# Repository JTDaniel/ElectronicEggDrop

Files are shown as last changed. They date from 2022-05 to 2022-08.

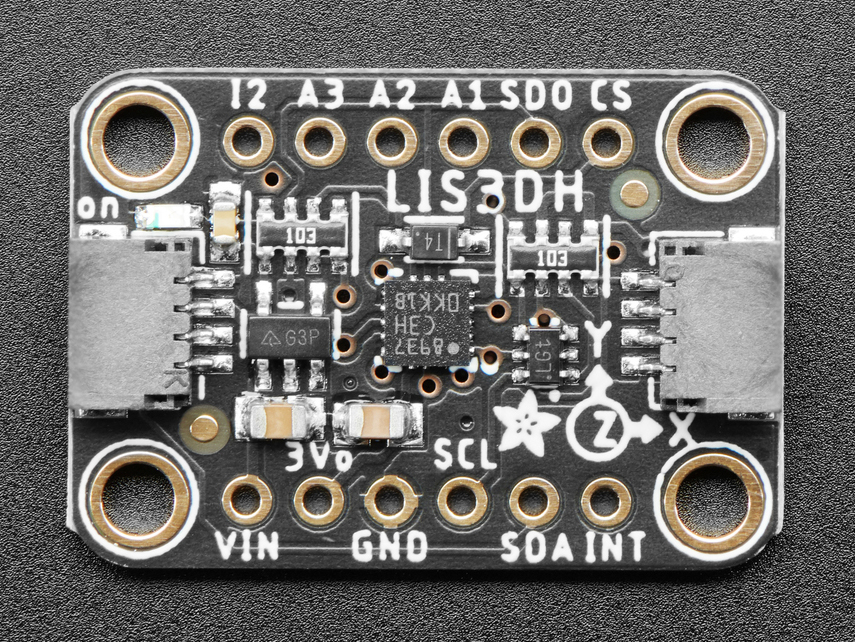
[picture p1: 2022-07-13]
Electronics/ImportedParts/Adafruit-LIS3DH-Breakout-PCB/Adafruit-LIS3DH-Breakout-PCB-master/assets/2809.jpg

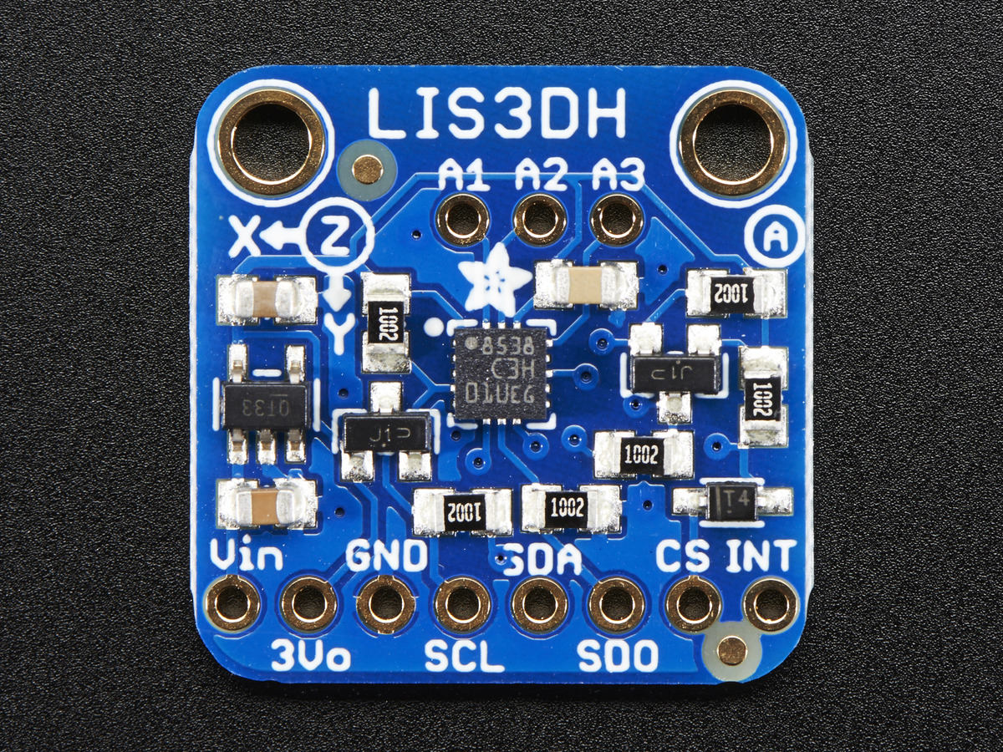
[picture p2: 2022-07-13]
Electronics/ImportedParts/Adafruit-LIS3DH-Breakout-PCB/Adafruit-LIS3DH-Breakout-PCB-master/assets/image.jpg

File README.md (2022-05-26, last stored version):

# ElectronicEggDrop
This is a project Pioneered by the Arizona State University MakerSpace workers, J. Travis Daniel, Gehrig Dixon, and Liam Nelson.  The goal is to make an egg drop experiment that is more sustainable than the regular use of this experiment in physics classrooms today.  This is being done by replacing regular edible egss with electronic sensor packages designed to look like an egg.

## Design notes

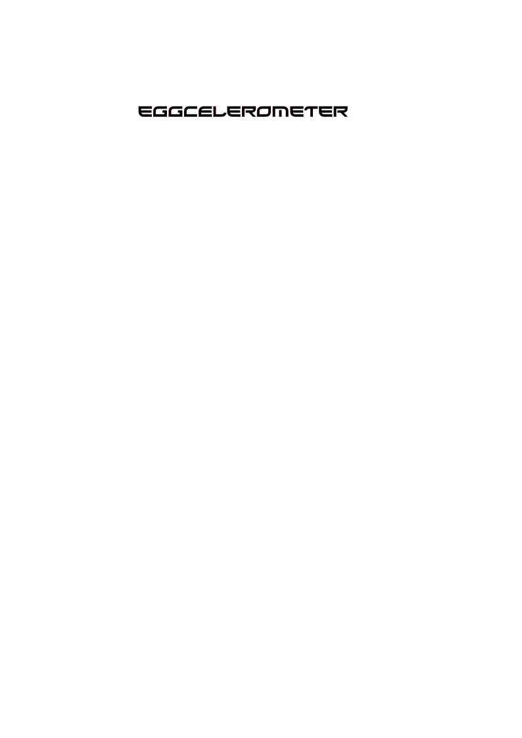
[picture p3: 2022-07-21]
Electronics/Graphics/Eggcelerometer.png

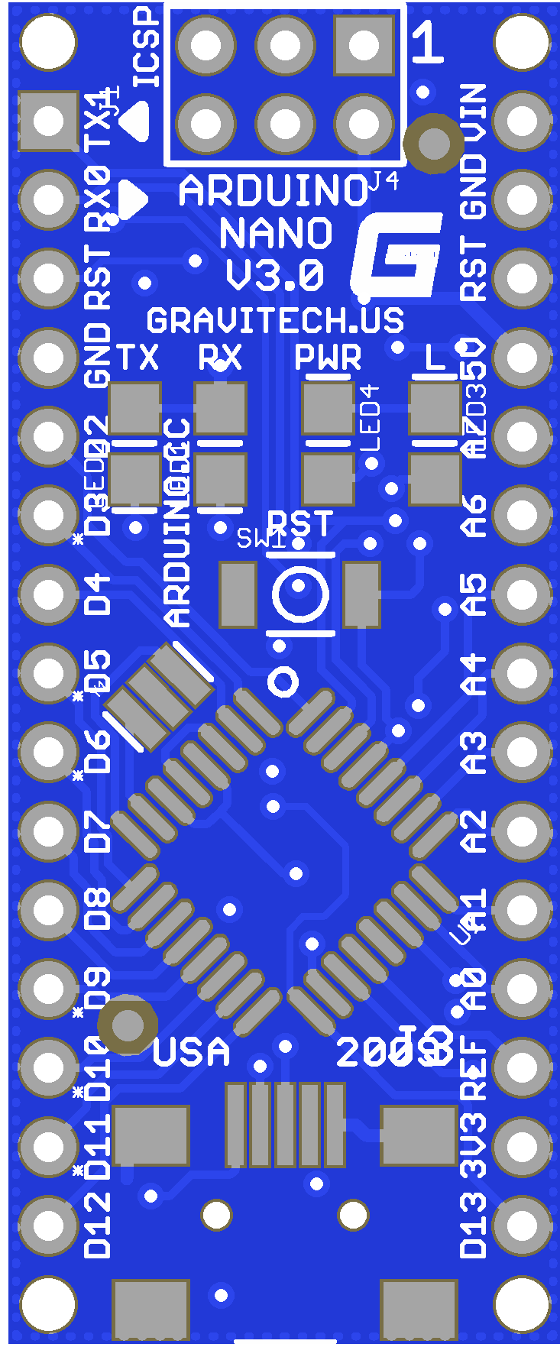
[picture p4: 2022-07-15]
3D_Models/Arduino Nano/Arduino Nano.png

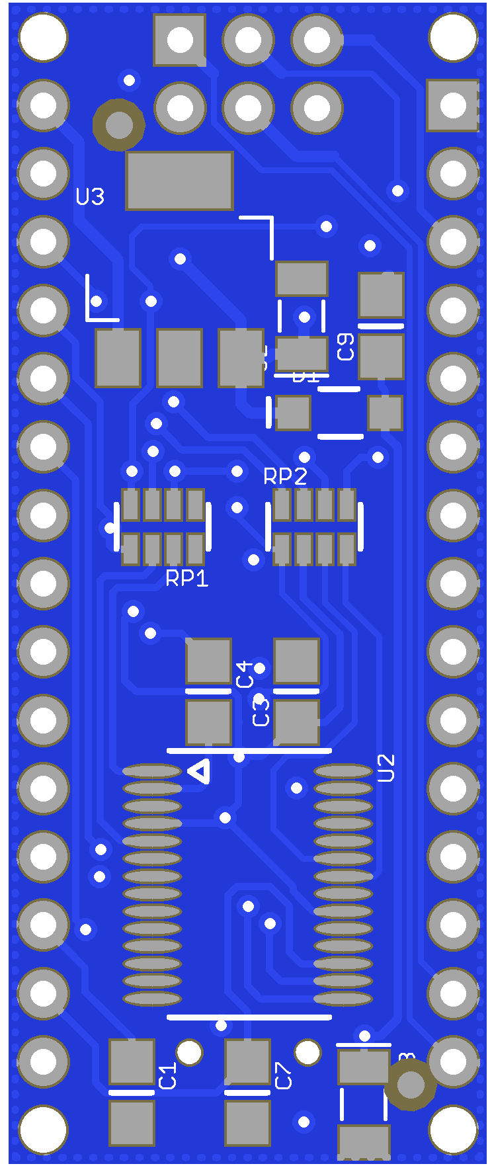
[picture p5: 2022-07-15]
3D_Models/Arduino Nano/Arduino Nano .png

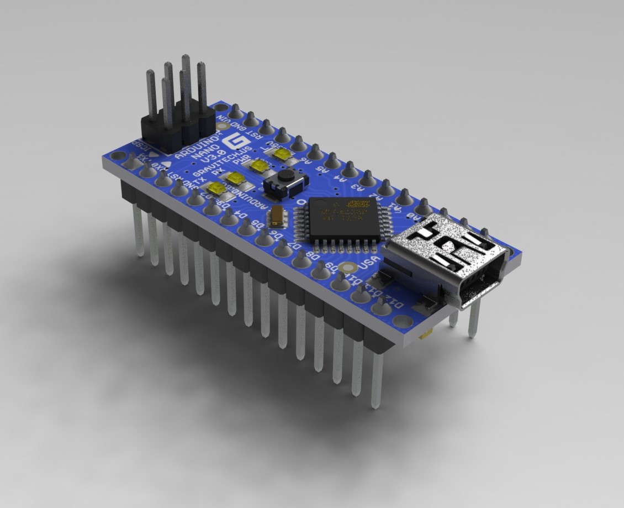
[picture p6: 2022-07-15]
3D_Models/Arduino Nano/Arduino Nano.JPG

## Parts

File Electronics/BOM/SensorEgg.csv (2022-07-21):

Id | Designator | Package | Quantity | Designation | Supplier and ref
1 | LIS3DH Connector,SD Card Reader Connector | PinHeader_1x06_P2.54mm_Vertical | 2 | Conn_01x06
2 |  |  | 1
3 | U1 | LIS3DH | 1 | LIS3DH
4 | U2 | SDCardReader | 1 | SDCardReader

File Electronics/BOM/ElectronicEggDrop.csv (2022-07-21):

Id | Designator | Package | Quantity | Designation | Supplier and ref
1 | Arduino Nano | MODULE_ABX00053 | 1 | ABX00053
2 | +3.7v,+3.7V | JST_PH_S2B-PH-K_1x02_P2.00mm_Horizontal | 2 | Screw_Terminal_01x02
3 | R2,R3,R1 | R_Axial_DIN0204_L3.6mm_D1.6mm_P5.08mm_Horizontal | 3 | R
4 | Indicator_LEDs1 | PinSocket_2x03_P2.54mm_Vertical | 1 | LED_RAGB
5 | Switch | PinSocket_1x02_P2.54mm_Vertical | 1 | SW_SPST
6 | LIS3DH Connector,SD Card Reader Connector | PinSocket_1x06_P2.54mm_Vertical | 2 | Conn_01x06_Male

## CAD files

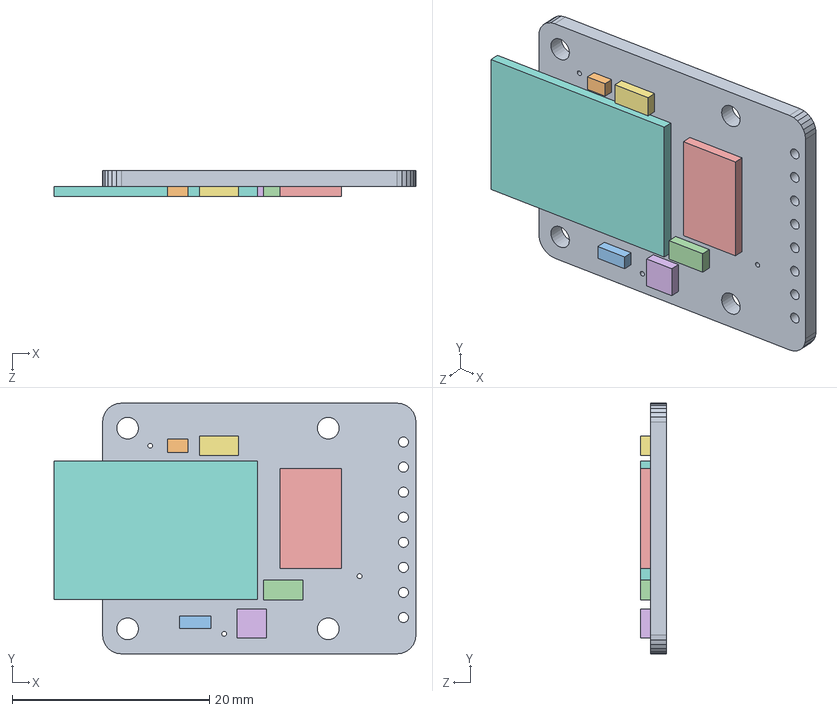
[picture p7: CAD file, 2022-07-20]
3D_Models/microsd/microsd.SLDASM
36.7 x 25.4 x 2.60 mm
microsd
CHIPLED0805_RED
A_321618R_10UF_10V
C0805K_0_1UF
SO16_4050D
SOT235L_LP298XS
R0805_1K
MICROSD_MICROSD

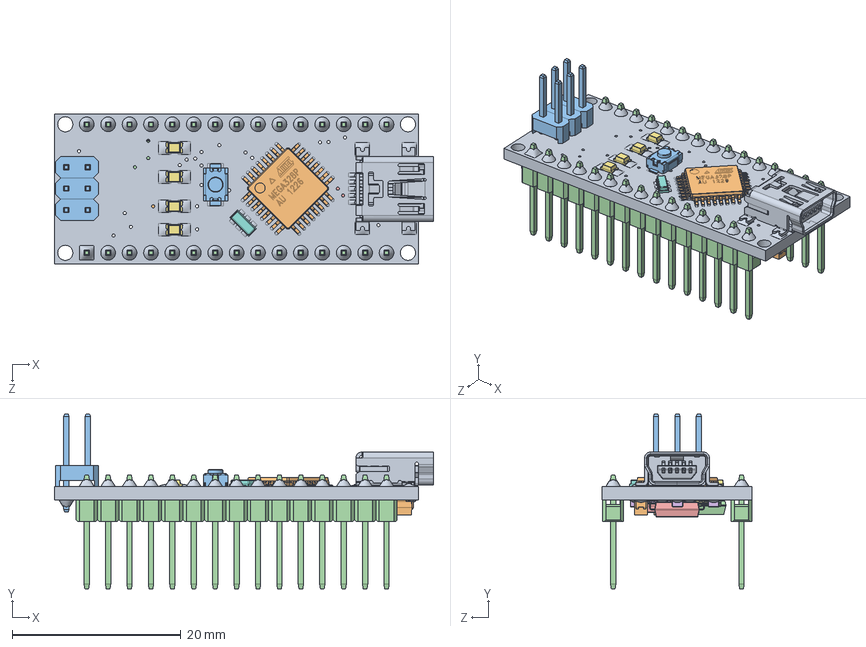
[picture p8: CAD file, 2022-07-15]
3D_Models/Arduino Nano/Arduino nano.SLDASM
45.0 x 20.7 x 17.8 mm
nano board
atmega328
PLD-2.step x 3
1x15 Male Pin Header x 2
FTDI FT232RL
User Library-C0805-2.step x 5
0805 Chip SMD LED (2x1.2mm).step x 4
SMD Crystal 16MHz
Mini B USB
Tantalum Capacitor 475C A3216 x 2
Pushbutton3x4x2
C5 FD10 Reg
Diode MBR0520
102 RESISTOR PACK
189 RESISTOR PACK

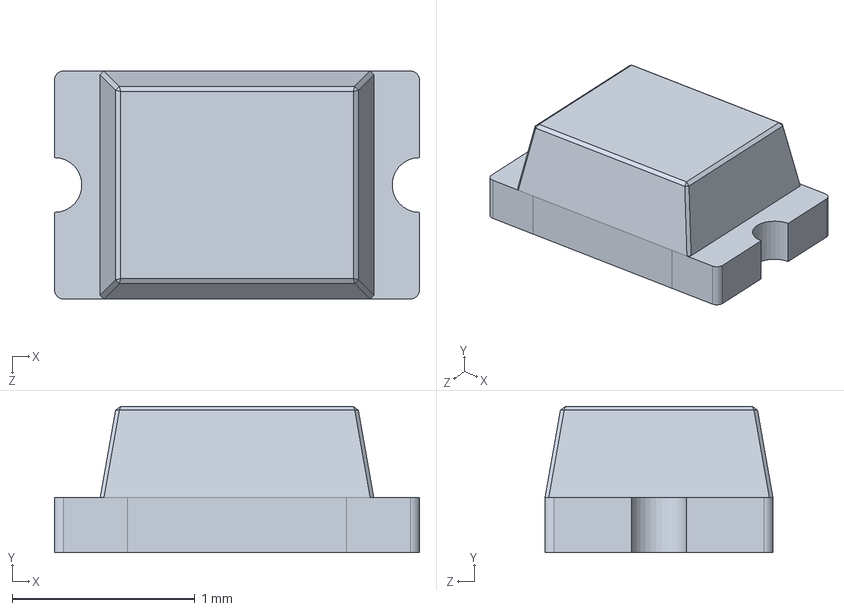
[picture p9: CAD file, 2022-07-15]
3D_Models/Arduino Nano/0805 Chip SMD LED (2x1.2mm).step.SLDPRT
2.00 x 0.8 x 1.25 mm

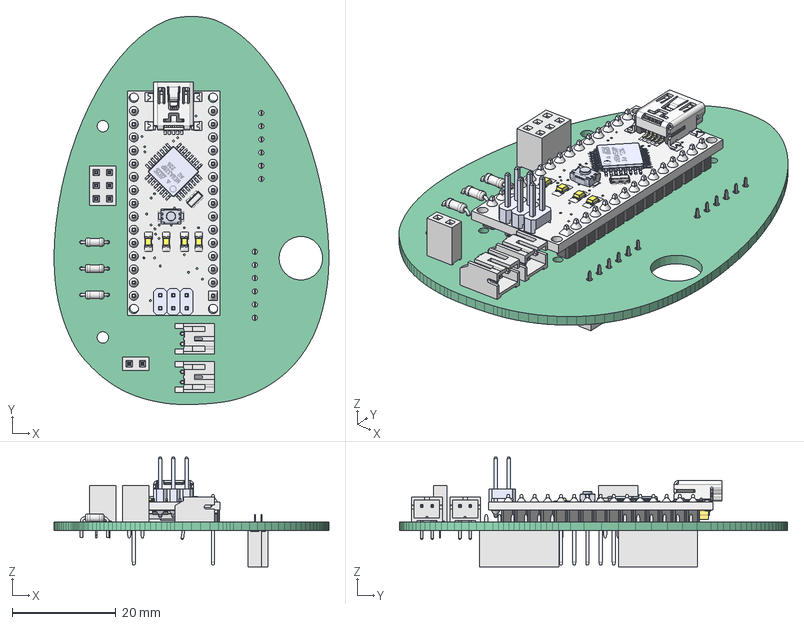
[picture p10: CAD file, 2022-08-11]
3D_Models/ControlEgg.FCStd
52.9 x 74.6 x 21.1 mm
Pcb_7da9
nano board
atmega328
PLD-2.step
PLD-2.step001
PLD-2.step002
1x15 Male Pin Header
1x15 Male Pin Header001
1x15 Male Pin Header002
1x15 Male Pin Header003
1x15 Male Pin Header004
1x15 Male Pin Header005
1x15 Male Pin Header006
1x15 Male Pin Header007
1x15 Male Pin Header008
1x15 Male Pin Header009
1x15 Male Pin Header010
1x15 Male Pin Header011
1x15 Male Pin Header012
1x15 Male Pin Header013
1x15 Male Pin Header014
1x15 Male Pin Header015
1x15 Male Pin Header017
1x15 Male Pin Header018
1x15 Male Pin Header019
1x15 Male Pin Header020
1x15 Male Pin Header021
1x15 Male Pin Header022
1x15 Male Pin Header023
1x15 Male Pin Header024
1x15 Male Pin Header025
1x15 Male Pin Header026
1x15 Male Pin Header027
1x15 Male Pin Header028
1x15 Male Pin Header029
1x15 Male Pin Header030
1x15 Male Pin Header031
1x15 Male Pin Header032
FTDI FT232RL
FTDI FT232RL001
FTDI FT232RL002
FTDI FT232RL003
FTDI FT232RL004
FTDI FT232RL005
FTDI FT232RL006
FTDI FT232RL007
FTDI FT232RL008
FTDI FT232RL009
FTDI FT232RL010
FTDI FT232RL011
FTDI FT232RL012
FTDI FT232RL013
FTDI FT232RL014
FTDI FT232RL015
FTDI FT232RL016
FTDI FT232RL017
FTDI FT232RL018
FTDI FT232RL019
FTDI FT232RL020
FTDI FT232RL021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

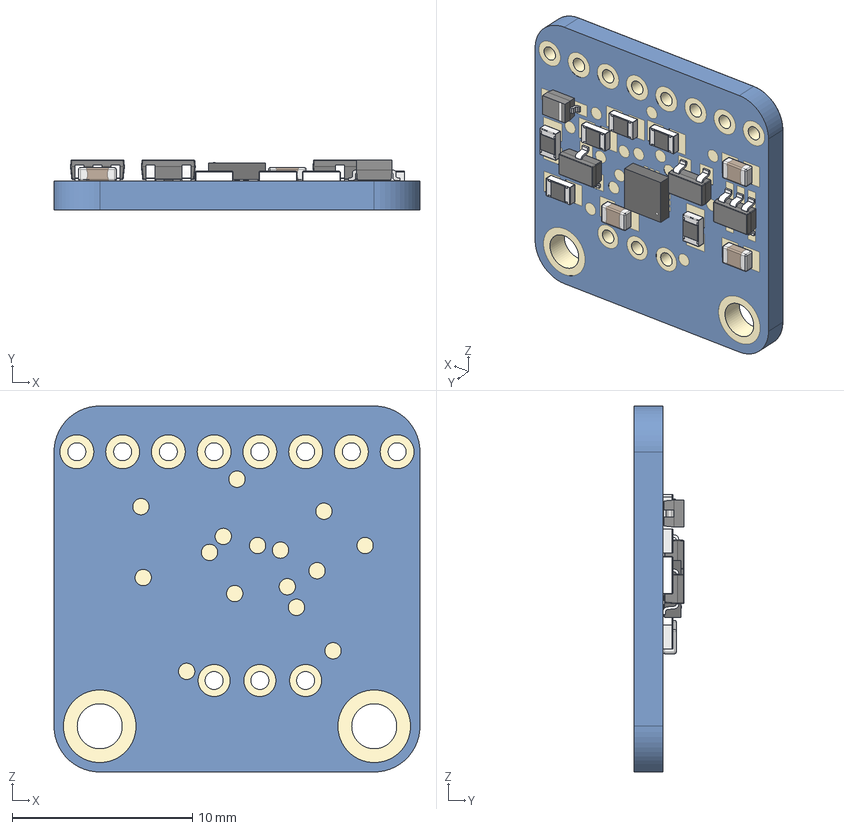
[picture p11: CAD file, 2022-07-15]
3D_Models/LIS3DH/LIS3DH v9.step
20.3 x 2.79 x 20.3 mm
SOT23-5
SOT23-3 x 2
16-LGA-3X3
SMD Resistor 0805 x 6
Cap 0805 x 3
SOD-323

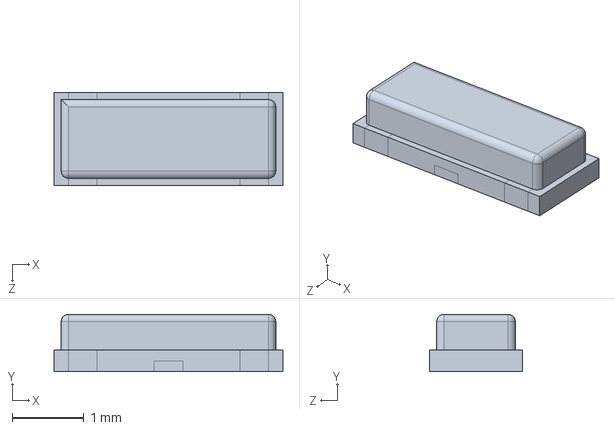
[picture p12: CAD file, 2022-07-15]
3D_Models/Arduino Nano/SMD Crystal 16MHz.SLDPRT
3.20 x 0.8 x 1.30 mm

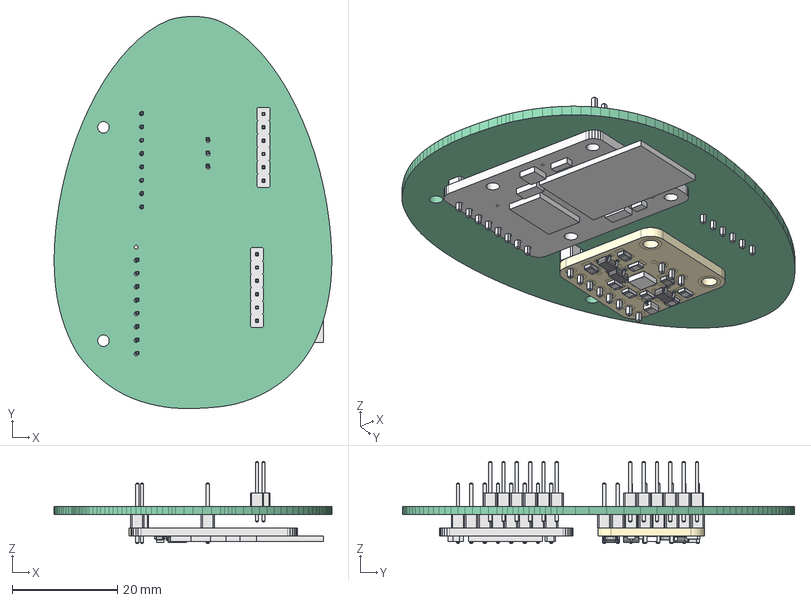
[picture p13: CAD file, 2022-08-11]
3D_Models/SensorEgg.FCStd
52.9 x 74.6 x 15.6 mm
Pcb_4512
LIS3DH Connector_PinHeader_1x06_P254mm_Vertical_2e8bbb15d2d6 x 2
SOT23-5 v1
SOT23-5 v002
SOT23-5 v003
SOT23-5 v004
SOT23-5 v005
SOT23-5 v006
SOT23-3 v1
SOT23-3 v002
SOT23-3 v003
SOT23-3 v004
SOT23-3 v006
SOT23-3 v007
SOT23-3 v008
SOT23-3 v009
16-LGA-3X3 v2
SMD Resistor 0805 v1
SMD Resistor 0805 v002
SMD Resistor 0805 v003
SMD Resistor 0805 v005
SMD Resistor 0805 v006
SMD Resistor 0805 v007
SMD Resistor 0805 v009
SMD Resistor 0805 v010
SMD Resistor 0805 v011
SMD Resistor 0805 v013
SMD Resistor 0805 v014
SMD Resistor 0805 v015
SMD Resistor 0805 v017
SMD Resistor 0805 v018
SMD Resistor 0805 v019
SMD Resistor 0805 v021
SMD Resistor 0805 v022
SMD Resistor 0805 v023
Cap 0805 v1
Cap 0805 v002
Cap 0805 v003
SOD-323 v1
U1_PinHeader_1x08_P254mm_Vertical_1ec43fbb1add[2] x 2
U1_PinHeader_1x03_P254mm_Vertical_1ec43fbb1add[3]
Ada microsd
Ada microsd001
Ada microsd002
Ada microsd003
Ada microsd004
Ada microsd005
Ada microsd006
Ada microsd007

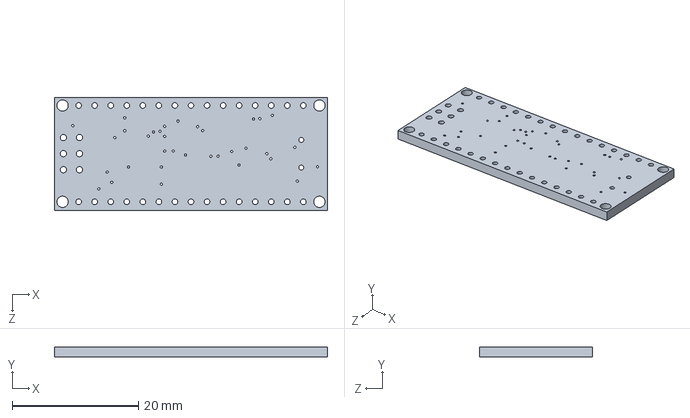
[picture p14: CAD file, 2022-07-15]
3D_Models/Arduino Nano/nano board.SLDPRT
43.2 x 1.60 x 17.8 mm

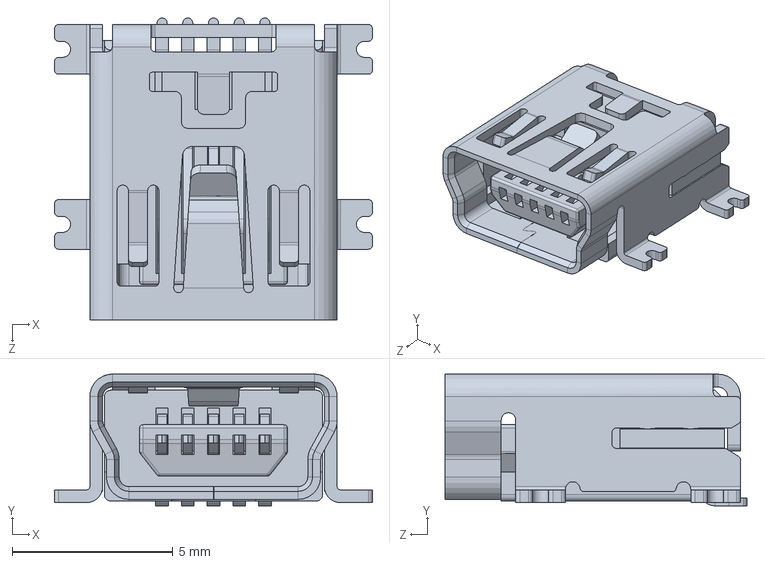
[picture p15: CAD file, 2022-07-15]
3D_Models/Arduino Nano/Mini B USB.SLDPRT
9.90 x 4.10 x 9.40 mm

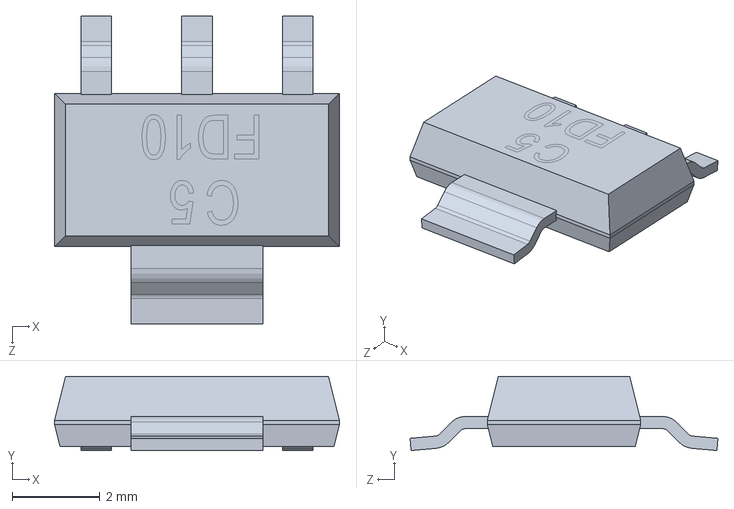
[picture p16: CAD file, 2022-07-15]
3D_Models/Arduino Nano/C5 FD10 Reg.SLDPRT
6.50 x 1.69 x 7.02 mm

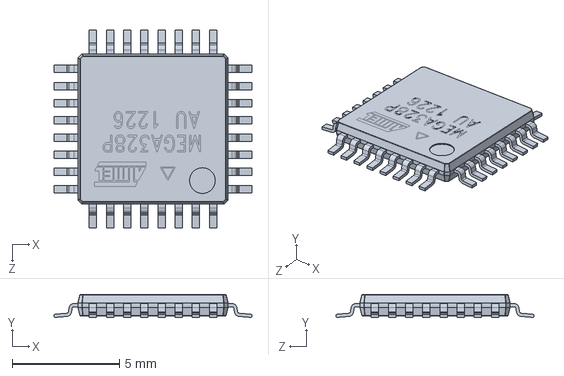
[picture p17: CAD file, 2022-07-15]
3D_Models/Arduino Nano/atmega328.SLDPRT
9.21 x 1.07 x 9.21 mm

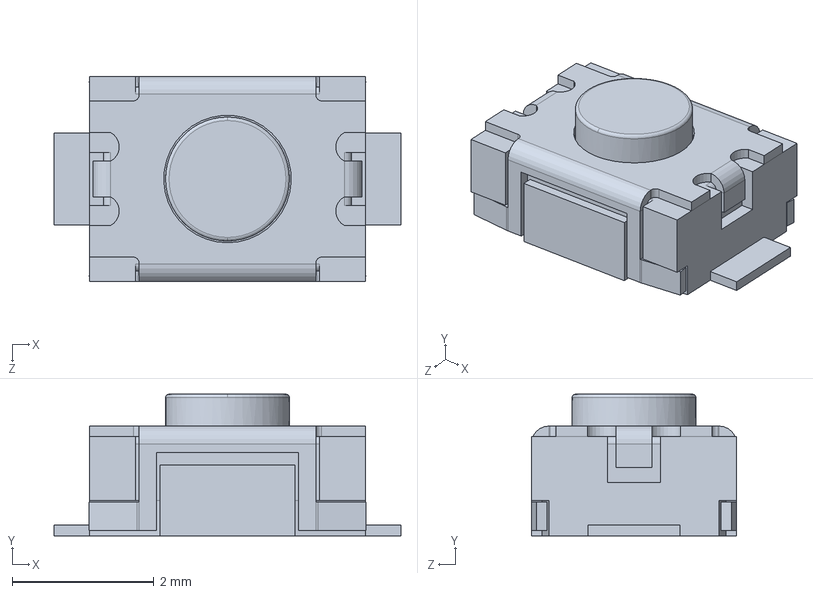
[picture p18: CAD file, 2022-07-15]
3D_Models/Arduino Nano/Pushbutton3x4x2.SLDPRT
4.90 x 2.00 x 2.90 mm

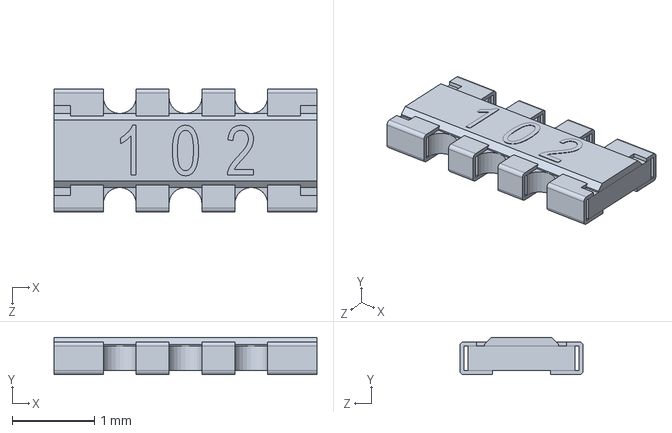
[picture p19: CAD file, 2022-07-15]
3D_Models/Arduino Nano/102 RESISTOR PACK.SLDPRT
3.20 x 0.455 x 1.50 mm

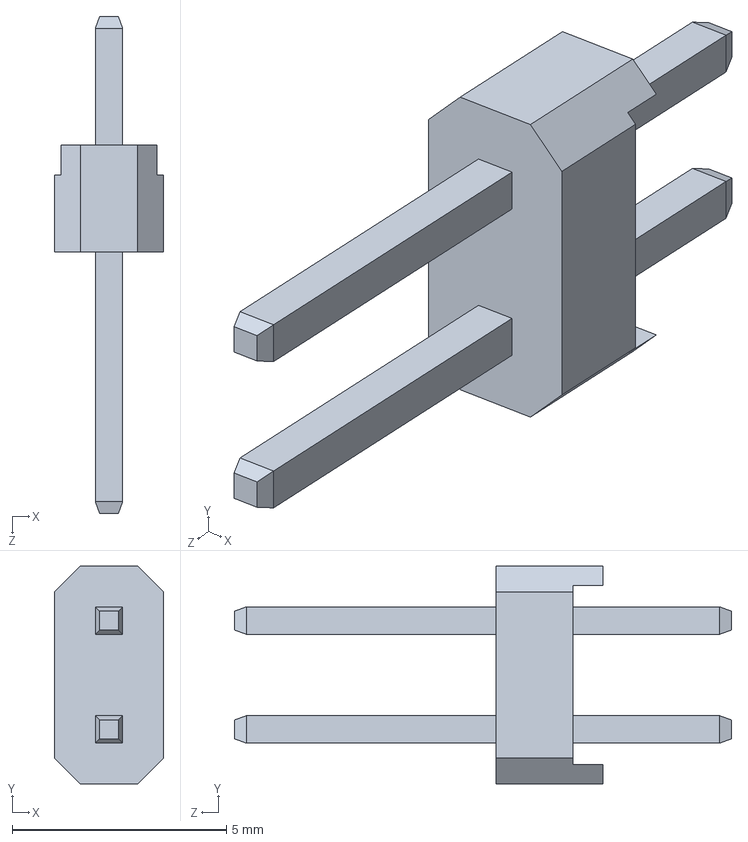
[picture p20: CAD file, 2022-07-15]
3D_Models/Arduino Nano/PLD-2.step.SLDPRT
2.54 x 5.08 x 11.6 mm

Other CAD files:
3D_Models/LIS3DH/LIS3DH.FCStd
3D_Models/microsd/Ada microsd.STEP
3D_Models/Arduino Nano/1x15 Male Pin Header.SLDPRT
3D_Models/Arduino Nano/Diode MBR0520.SLDPRT
3D_Models/Arduino Nano/189 RESISTOR PACK.SLDPRT
3D_Models/Arduino Nano/ArduinoNano.FCStd
3D_Models/Arduino Nano/FTDI FT232RL.SLDPRT
3D_Models/Arduino Nano/Tantalum Capacitor 475C A3216.SLDPRT
3D_Models/Arduino Nano/User Library-C0805-2.step.SLDPRT
3D_Models/microsd/Ada microsd.SLDPRT
Electronics/ElectronicEggDropV1/SensorEgg/SensorEgg.step

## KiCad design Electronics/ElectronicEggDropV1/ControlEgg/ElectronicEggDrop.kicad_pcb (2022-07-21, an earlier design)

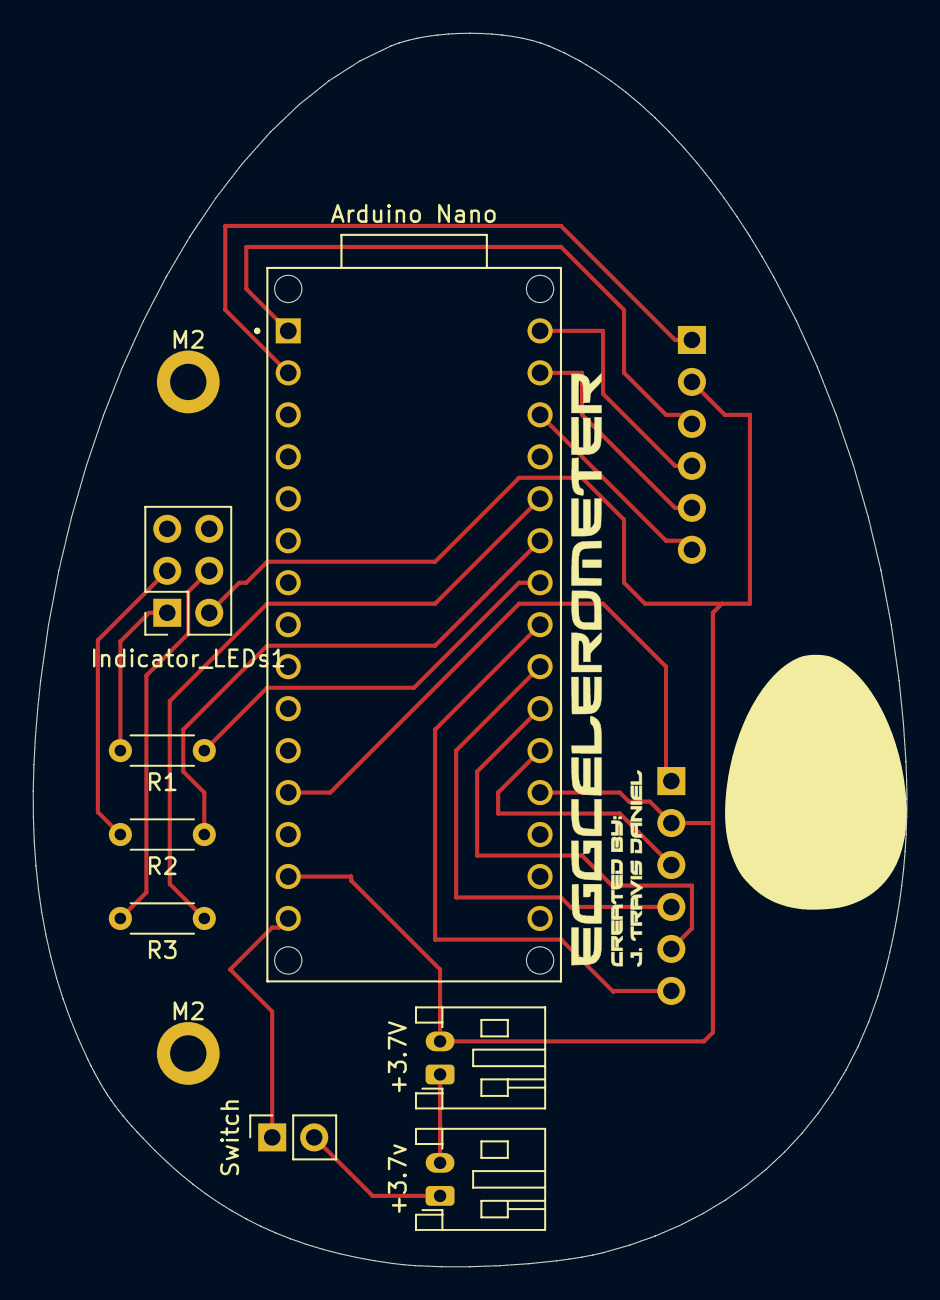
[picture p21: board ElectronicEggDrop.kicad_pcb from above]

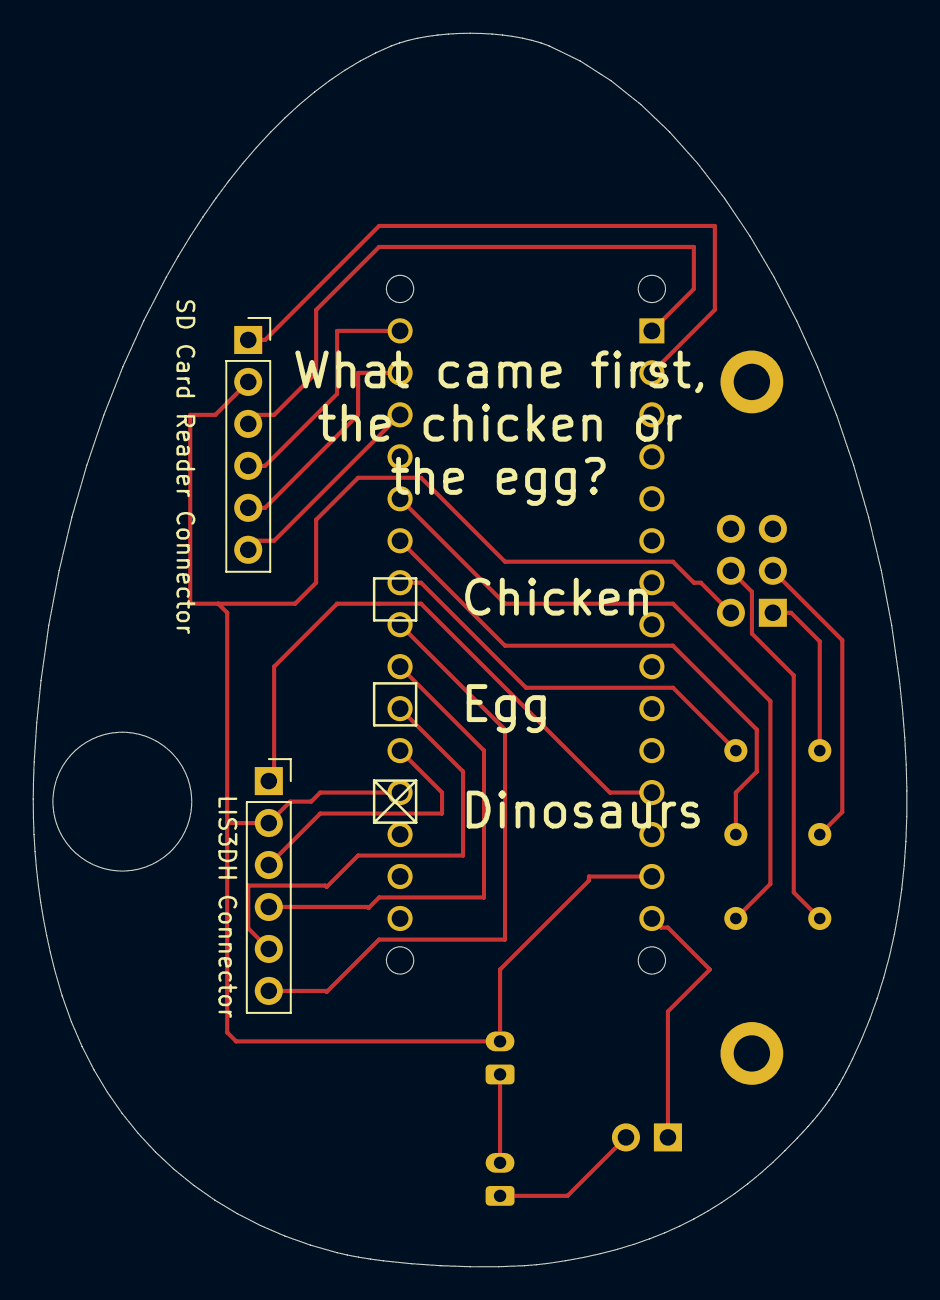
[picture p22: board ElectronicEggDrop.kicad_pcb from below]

Board: 2 copper layers, 52.9 x 74.6 mm, 10 parts (2 on the bottom side), 20 nets.

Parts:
+3.7V, +3.7v: Screw_Terminal_01x02; JST_PH_S2B-PH-K_1x02_P2.00mm_Horizontal
Arduino Nano: ABX00053; MODULE_ABX00053
Indicator_LEDs1: LED_RAGB; PinSocket_2x03_P2.54mm_Vertical
LIS3DH Connector: Conn_01x06_Male; PinSocket_1x06_P2.54mm_Vertical
R1, R2, R3: R; R_Axial_DIN0204_L3.6mm_D1.6mm_P5.08mm_Horizontal
SD Card Reader Connector: Conn_01x06_Male; PinSocket_1x06_P2.54mm_Vertical
Switch: SW_SPST; PinSocket_1x02_P2.54mm_Vertical

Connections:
GND: +3.7V.2, Arduino Nano.14 (GND), Arduino Nano.19 (GND), Indicator_LEDs1.2 (A), LIS3DH Connector.2, SD Card Reader Connector.2
unnamed: Arduino Nano.1 (D13/GPIO6), SD Card Reader Connector.3
unnamed: Arduino Nano.2 (+3V3), SD Card Reader Connector.1
unnamed: Arduino Nano.12 (+5V), LIS3DH Connector.1
unnamed: Arduino Nano.15 (VIN), Switch.1 (A)
unnamed: Arduino Nano.20 (D2/GPIO25), LIS3DH Connector.3
unnamed: Arduino Nano.21 (D3/GPIO15), LIS3DH Connector.5
unnamed: Arduino Nano.22 (D4/GPIO26), LIS3DH Connector.4
unnamed: Arduino Nano.23 (D5/GPIO17), LIS3DH Connector.6
unnamed: Arduino Nano.24 (D6/GPIO18), R1.1
unnamed: Arduino Nano.25 (D7/GPIO19), R2.1
unnamed: Arduino Nano.26 (D8/GPIO20), R3.1
unnamed: Arduino Nano.28 (D10/GPIO5), SD Card Reader Connector.6
unnamed: Arduino Nano.29 (D11/GPIO7/COPI), SD Card Reader Connector.5
unnamed: Arduino Nano.30 (D12/GPIO4/CIPO), SD Card Reader Connector.4
unnamed: Indicator_LEDs1.1 (RK), R1.2
unnamed: Indicator_LEDs1.3 (GK), R2.2
unnamed: Indicator_LEDs1.4 (BK), R3.2
unnamed: +3.7v.1, Switch.2 (B)
unnamed: +3.7V.1, +3.7v.2

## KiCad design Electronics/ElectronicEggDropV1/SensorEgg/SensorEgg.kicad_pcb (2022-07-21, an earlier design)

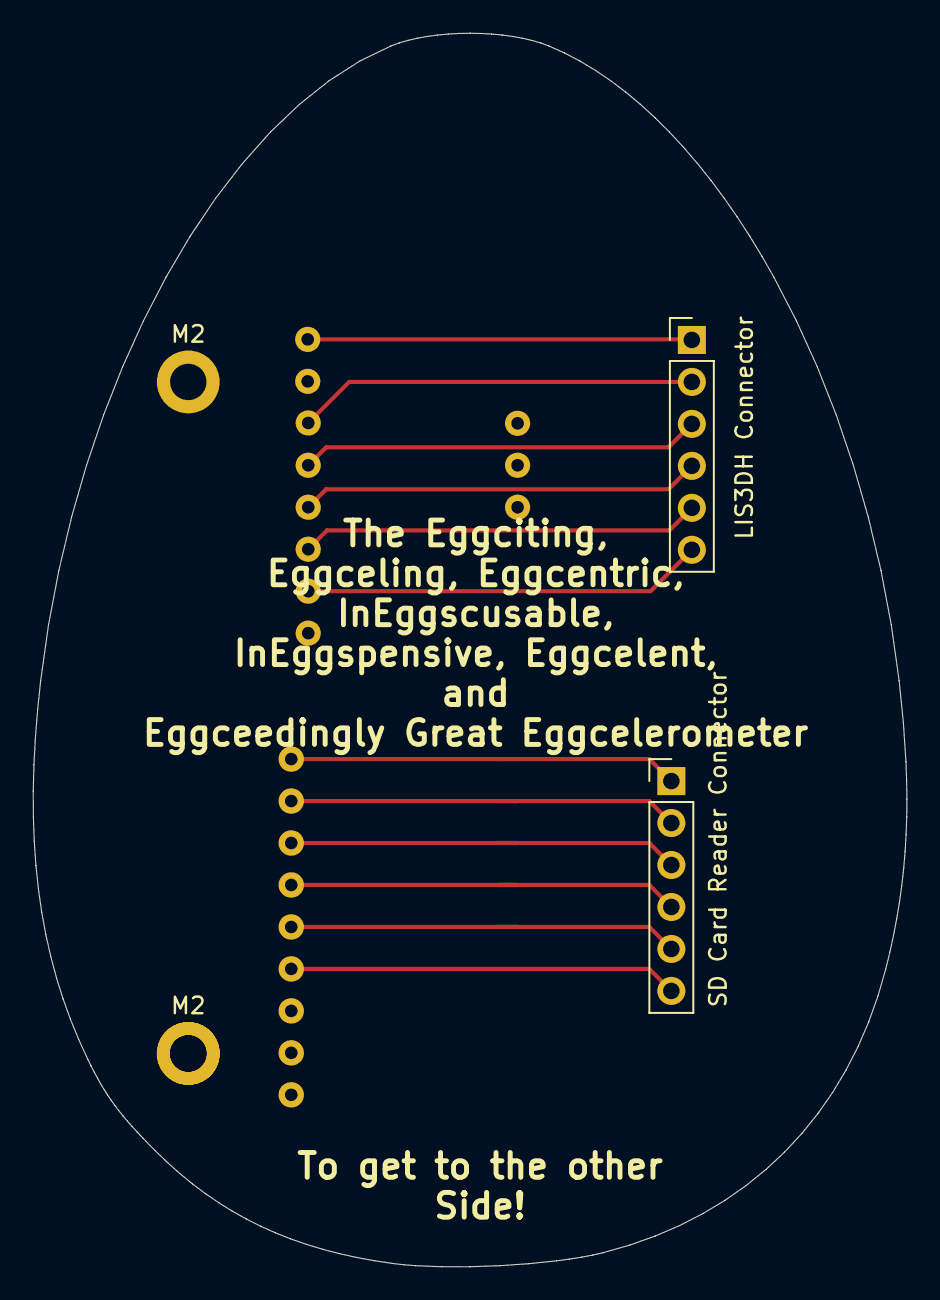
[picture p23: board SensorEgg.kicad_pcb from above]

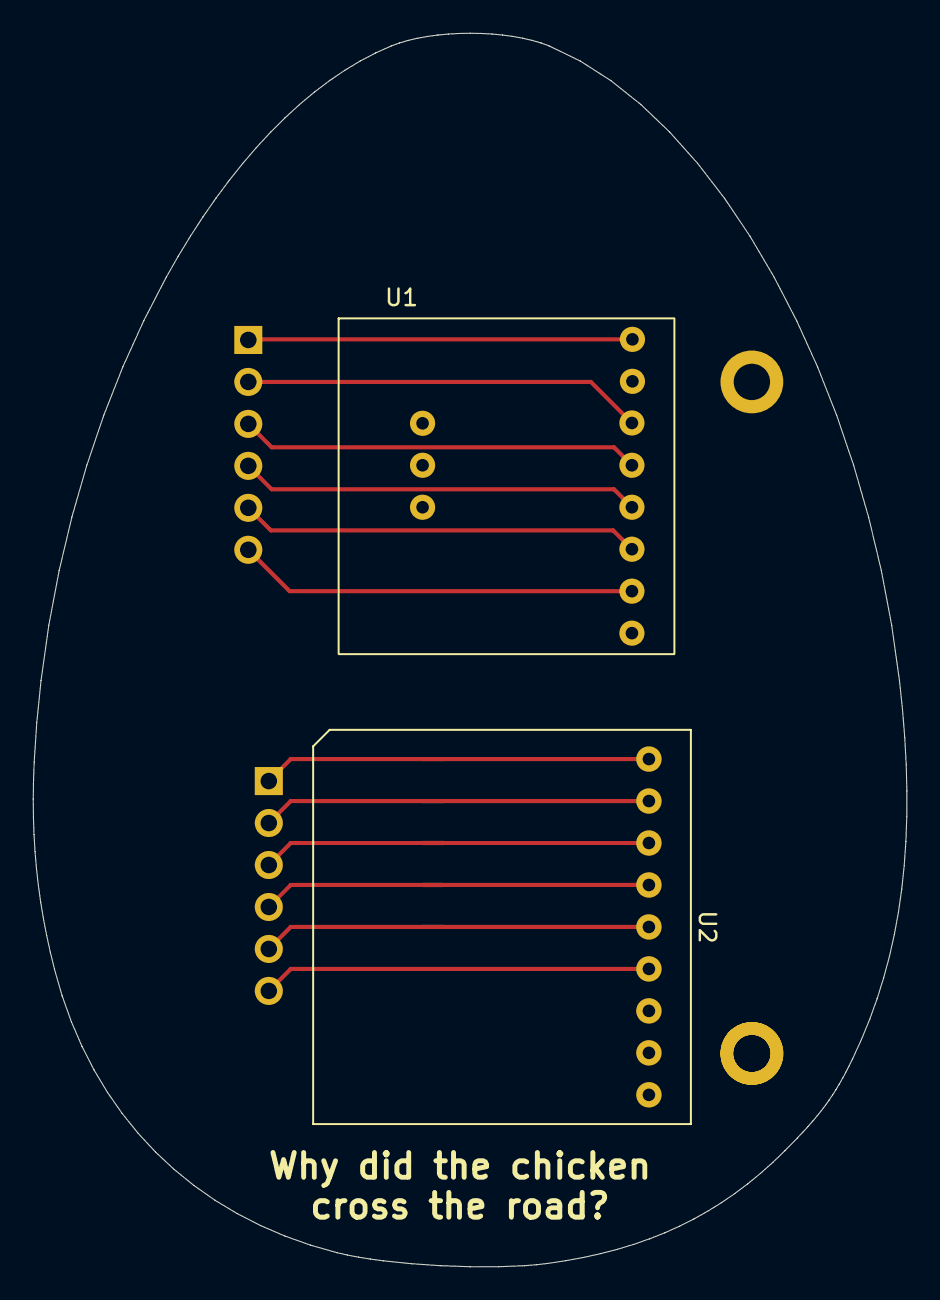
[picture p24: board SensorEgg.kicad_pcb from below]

Board: 2 copper layers, 52.9 x 74.6 mm, 6 parts (2 on the bottom side), 12 nets.

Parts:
LIS3DH Connector: Conn_01x06; PinHeader_1x06_P2.54mm_Vertical
M2, M2#2: MountingHole_2.2mm_M2_DIN965_Pad
SD Card Reader Connector: Conn_01x06; PinHeader_1x06_P2.54mm_Vertical
U1: LIS3DH
U2: SDCardReader

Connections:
unnamed: LIS3DH Connector.1, U1.1 (Vin)
unnamed: LIS3DH Connector.2, U1.3 (GND)
unnamed: LIS3DH Connector.3, U1.4 (SCL)
unnamed: LIS3DH Connector.4, U1.5 (SDA)
unnamed: LIS3DH Connector.5, U1.6 (SDO)
unnamed: LIS3DH Connector.6, U1.7 (CS)
unnamed: SD Card Reader Connector.1, U2.1 (3V)
unnamed: SD Card Reader Connector.2, U2.2 (GND)
unnamed: SD Card Reader Connector.3, U2.3 (CLK)
unnamed: SD Card Reader Connector.4, U2.4 (D0/SO)
unnamed: SD Card Reader Connector.5, U2.5 (CMD/SI)
unnamed: SD Card Reader Connector.6, U2.6 (D3/CS)

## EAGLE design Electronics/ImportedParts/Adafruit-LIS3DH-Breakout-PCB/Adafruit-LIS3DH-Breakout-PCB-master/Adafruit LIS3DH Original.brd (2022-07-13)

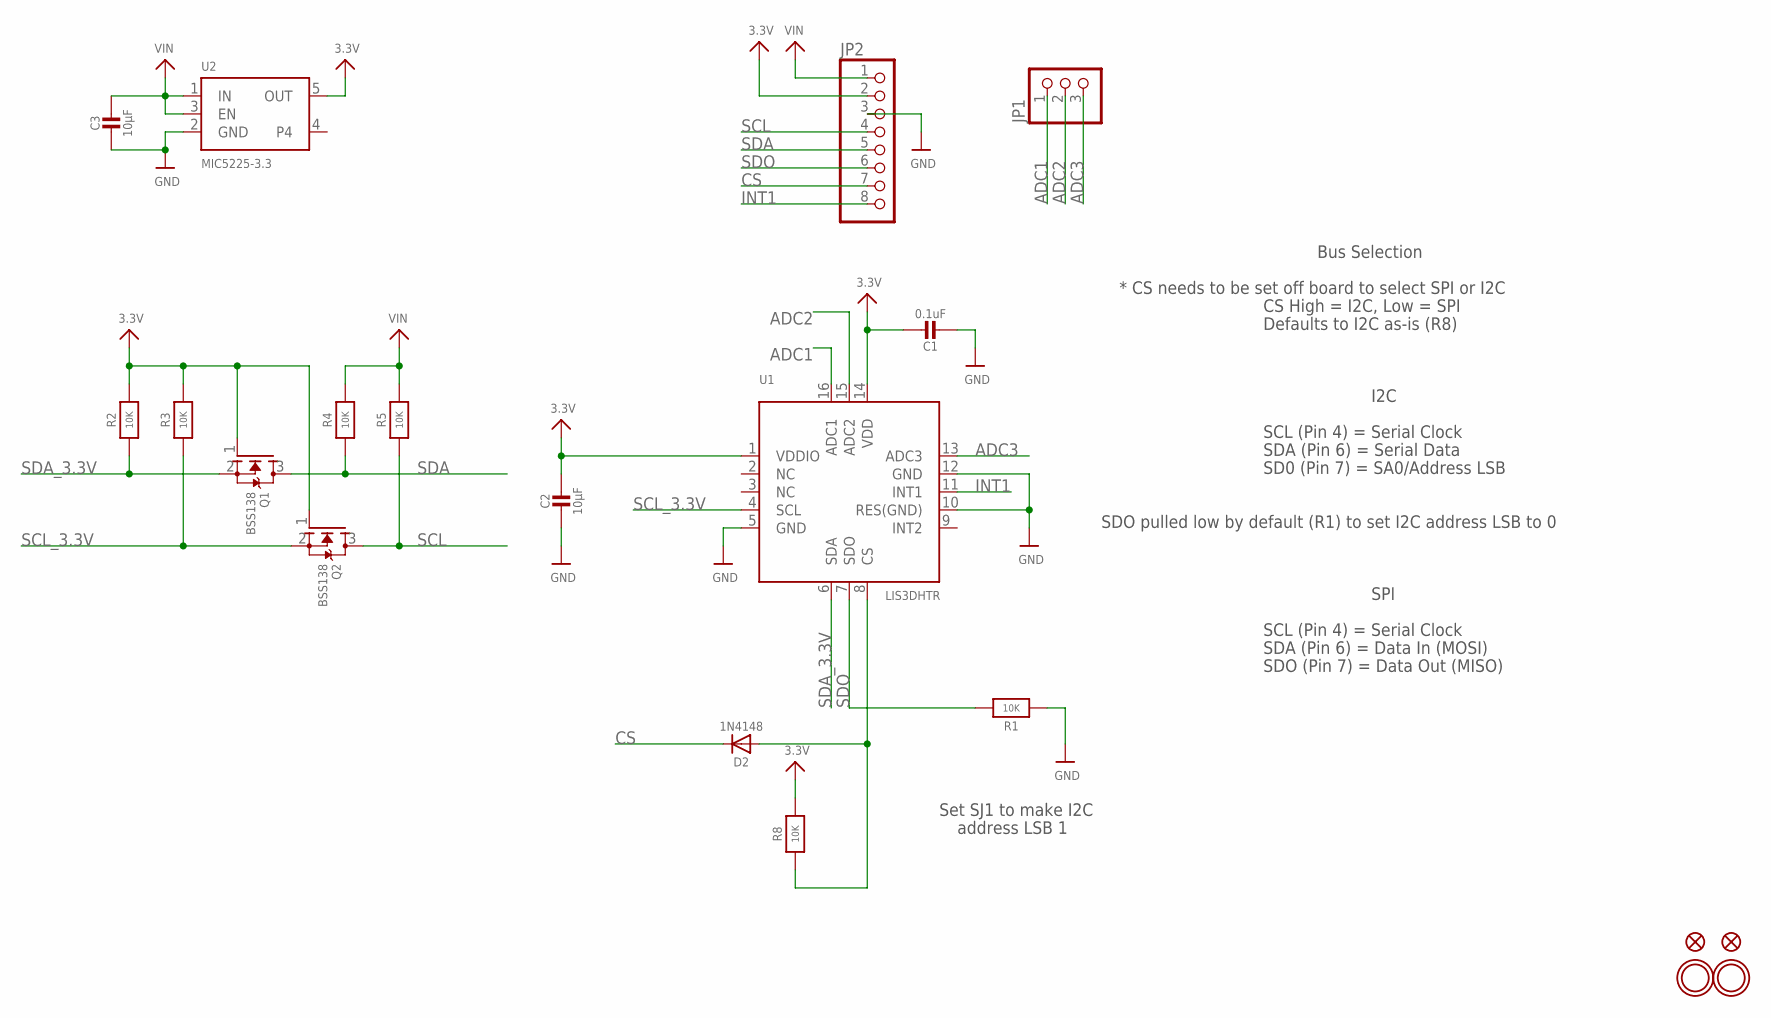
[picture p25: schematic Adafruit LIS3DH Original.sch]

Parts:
C1: 0.1uF; 0805_10MGAP
C2, C3: 10µF; 0805-NO
D2: 1N4148; SOD-323
FID1, FID2: FIDUCIAL""; FIDUCIAL_1MM
JP1: HEADER-1X3ROUND; 1X03_ROUND
JP2: HEADER-1X870MIL; 1X08_ROUND_70
Q1, Q2: BSS138; SOT23-WIDE
R1, R2, R3, R4, R5, R8: 10K; 0805-NO
U1: LIS3DHTR; LGA16_3X3MM
U2: MIC5225-3.3; SOT23-5
U$10, U$13: MOUNTINGHOLE2.5; MOUNTINGHOLE_2.5_PLATED

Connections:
3.3V: C1.1, C2.1, JP2.2, Q1.1 (G), Q2.1 (G), R2.2, R3.2, R8.2, U1.1 (VDDIO), U1.14 (VDD), U2.5 (OUT)
ADC1: JP1.1, U1.16 (ADC1)
ADC2: JP1.2, U1.15 (ADC2)
ADC3: JP1.3, U1.13 (ADC3)
CS: D2.C, JP2.7
GND: C1.2, C2.2, C3.2, JP2.3, R1.1, U1.5 (GND), U1.10 (RES(GND)), U1.12 (GND), U2.2 (GND)
INT1: JP2.8, U1.11 (INT1)
unnamed: D2.A, R8.1, U1.8 (CS)
SCL: JP2.4, Q2.3 (D), R5.1
SCL_3.3V: Q2.2 (S), R3.1, U1.4 (SCL)
SDA: JP2.5, Q1.3 (D), R4.1
SDA_3.3V: Q1.2 (S), R2.1, U1.6 (SDA)
SDO: JP2.6, R1.2, U1.7 (SDO)
VIN: C3.1, JP2.1, R4.2, R5.2, U2.1 (IN), U2.3 (EN)

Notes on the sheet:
I2C
SCL (Pin 4) = Serial Clock
SDA (Pin 6) = Serial Data
SD0 (Pin 7) = SA0/Address LSB
* CS needs to be set off board to select SPI or I2C
CS High = I2C, Low = SPI
Defaults to I2C as-is (R8)
SDO pulled low by default (R1) to set I2C address LSB to 0
Bus Selection
SPI
SDA (Pin 6) = Data In (MOSI)
SDO (Pin 7) = Data Out (MISO)
Set SJ1 to make I2C
address LSB 1

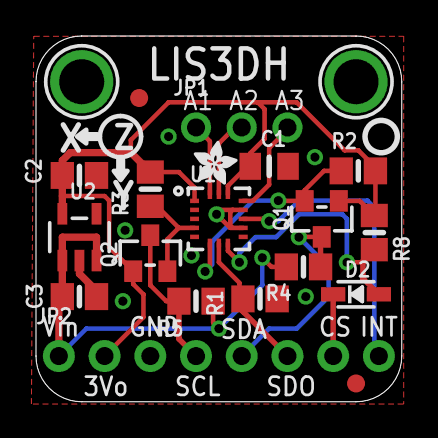
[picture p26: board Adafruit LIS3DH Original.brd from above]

Board: 2 copper layers, 20.3 x 20.3 mm, 23 parts (1 on the bottom side), 14 nets.

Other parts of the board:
U$9: PCBFEAT-REV-040
U$21: ADAFRUIT_2.5MM
U$22: ADAFRUIT_5MM

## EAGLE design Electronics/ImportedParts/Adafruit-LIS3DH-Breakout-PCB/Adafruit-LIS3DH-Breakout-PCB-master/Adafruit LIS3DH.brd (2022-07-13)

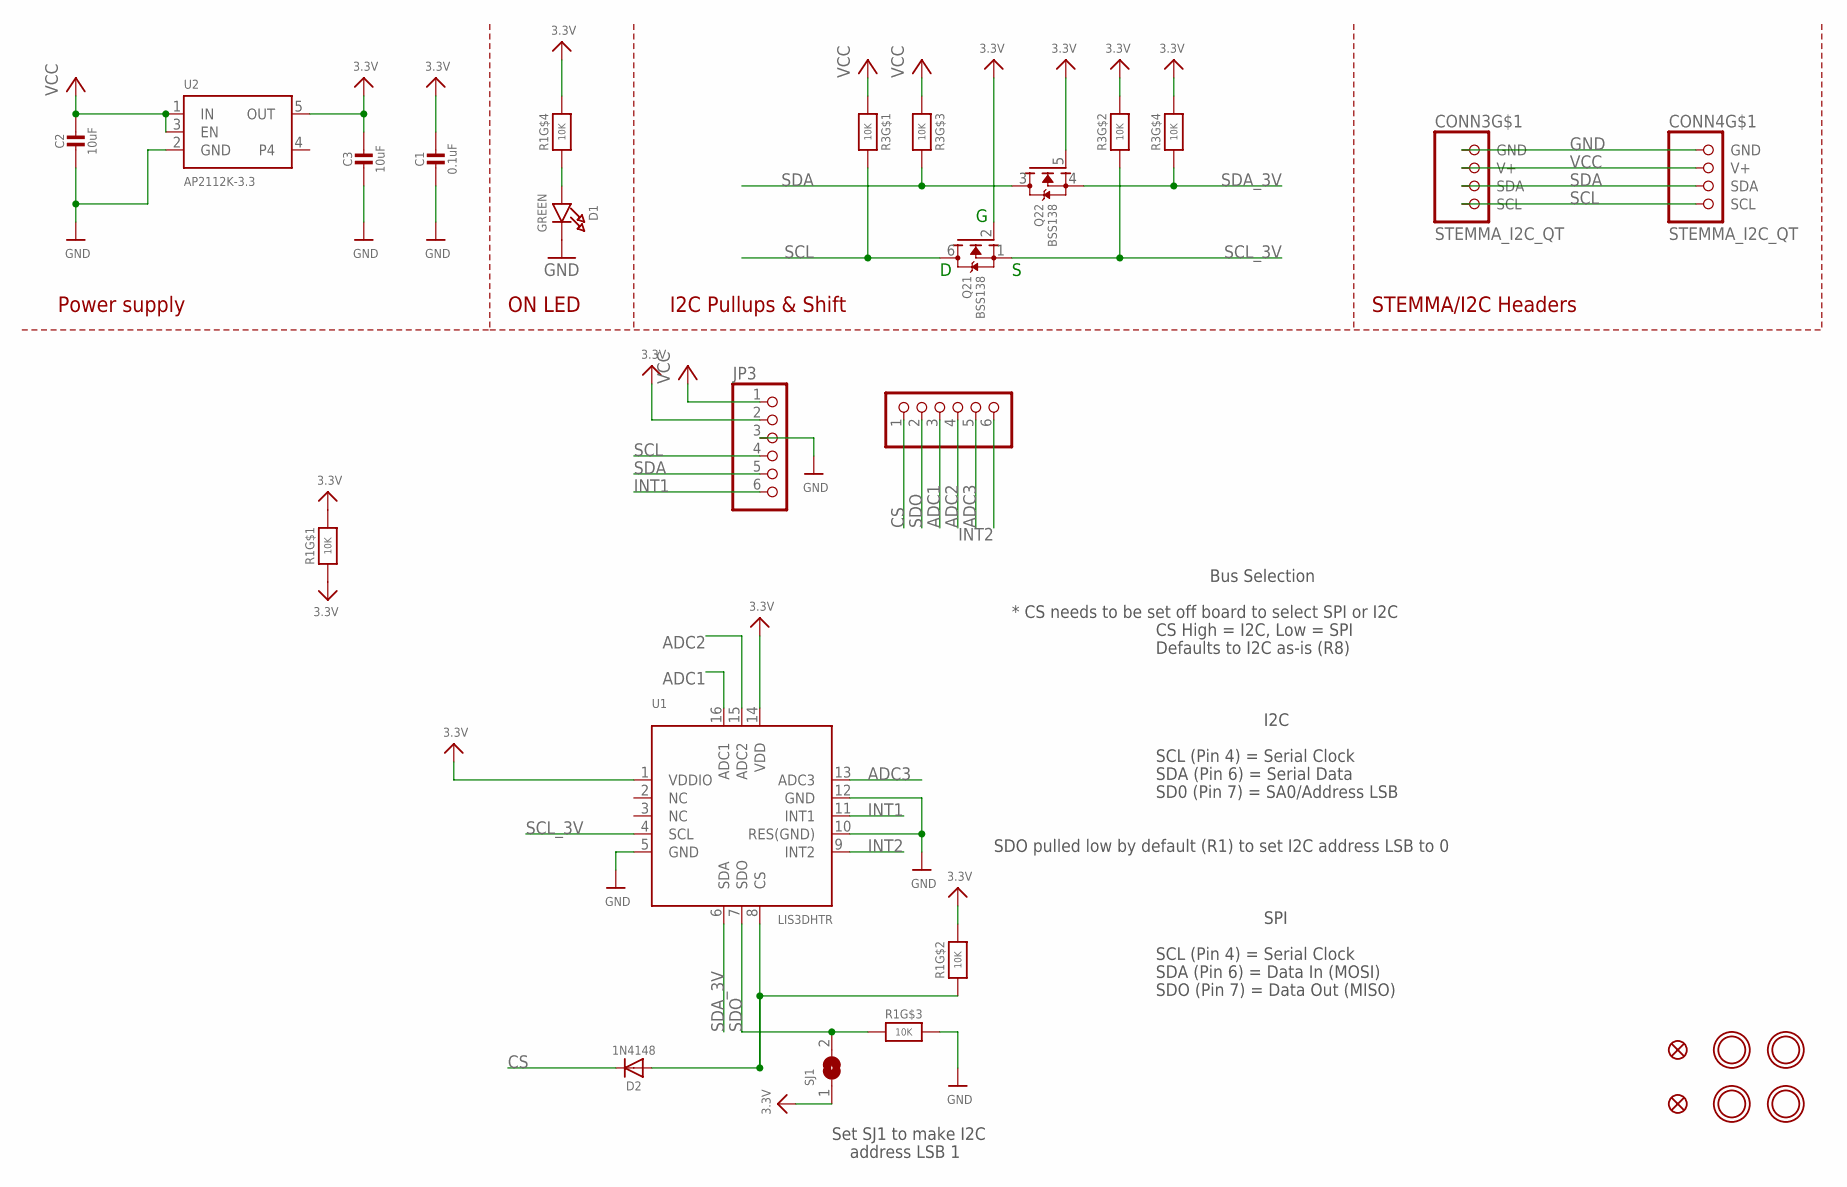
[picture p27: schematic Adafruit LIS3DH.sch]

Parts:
C1: 0.1uF; 0603-NO
C2, C3: 10uF; 0805-NO
CONN3, CONN4: STEMMA_I2C_QT; JST_SH4
D1: GREEN; CHIPLED_0603_NOOUTLINE
D2: 1N4148; SOD-323
FID3, FID4: FIDUCIAL_1MM
JP2, JP3: HEADER-1X670MIL; 1X06_ROUND_70
Q2: BSS138; SOT363
R1, R3: 10K; RESPACK_4X0603
SJ1: SOLDERJUMPER; SOLDERJUMPER_ARROW_NOPASTE
U1: LIS3DHTR; LGA16_3X3MM
U2: AP2112K-3.3; SOT23-5
U$1, U$17, U$19, U$21: MOUNTINGHOLE2.5; MOUNTINGHOLE_2.5_PLATED

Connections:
3.3V: C1.1, C3.1, JP3.2, Q2.2 (G), Q2.5 (G), R1.1, R1.5 (2), R1.7 (2), R1.8 (2), R3.2 (1), R3.4 (1), SJ1.1, U1.1 (VDDIO), U1.14 (VDD), U2.5 (OUT)
ADC1: JP2.3, U1.16 (ADC1)
ADC2: JP2.4, U1.15 (ADC2)
ADC3: JP2.5, U1.13 (ADC3)
CS: D2.C, JP2.1
GND: C1.2, C2.2, C3.2, CONN3.1 (GND), CONN4.1 (GND), D1.C, JP3.3, R1.6 (2), U1.5 (GND), U1.10 (RES(GND)), U1.12 (GND), U2.2 (GND)
INT1: JP3.6, U1.11 (INT1)
INT2: JP2.6, U1.9 (INT2)
unnamed: D1.A, R1.4 (1)
unnamed: D2.A, R1.2 (1), U1.8 (CS)
SCL: CONN3.4 (SCL), CONN4.4 (SCL), JP3.4, Q2.6 (D), R3.8 (2)
SCL_3V: Q2.1 (S), R3.7 (2), U1.4 (SCL)
SDA: CONN3.3 (SDA), CONN4.3 (SDA), JP3.5, Q2.3 (D), R3.6 (2)
SDA_3V: Q2.4 (S), R3.5 (2), U1.6 (SDA)
SDO: JP2.2, R1.3 (1), SJ1.2, U1.7 (SDO)
VCC: C2.1, CONN3.2 (V+), CONN4.2 (V+), JP3.1, R3.1, R3.3 (1), U2.1 (IN), U2.3 (EN)

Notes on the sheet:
I2C Pullups & Shift
STEMMA/I2C Headers
ON LED
Power supply
I2C
SCL (Pin 4) = Serial Clock
SDA (Pin 6) = Serial Data
SD0 (Pin 7) = SA0/Address LSB
* CS needs to be set off board to select SPI or I2C
CS High = I2C, Low = SPI
Defaults to I2C as-is (R8)
SDO pulled low by default (R1) to set I2C address LSB to 0
Bus Selection
SPI
SDA (Pin 6) = Data In (MOSI)
SDO (Pin 7) = Data Out (MISO)
Set SJ1 to make I2C
address LSB 1

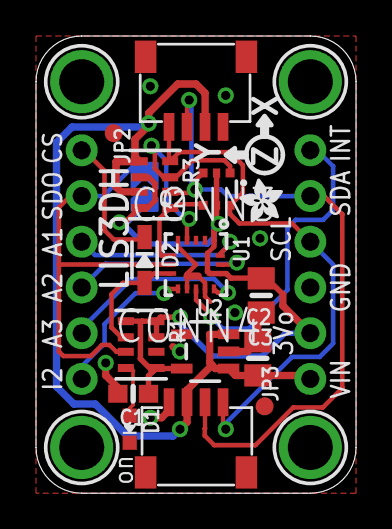
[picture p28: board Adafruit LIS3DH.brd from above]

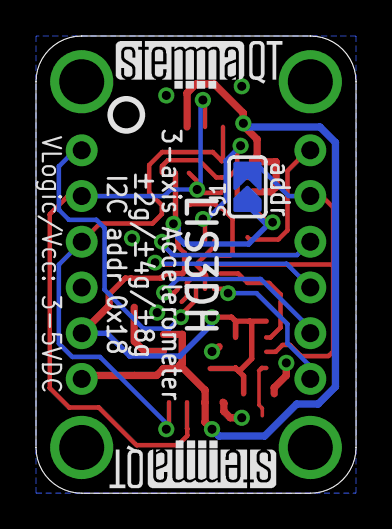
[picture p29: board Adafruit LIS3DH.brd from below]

Board: 2 copper layers, 17.8 x 25.4 mm, 25 parts (4 on the bottom side), 16 nets.

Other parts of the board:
U$12: ADAFRUIT_2.5MM
U$25: PCBFEAT-REV-040
U$30, U$31: STEMMAQT

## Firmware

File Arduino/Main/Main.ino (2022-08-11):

#include <Wire.h>
#include <SPI.h>
#include <Adafruit_LIS3DH.h>
#include <Adafruit_Sensor.h>
#include <SD.h>

// Used for software SPI
#define LIS3DH_CLK 2
#define LIS3DH_MISO 3
#define LIS3DH_MOSI 4
// Used for hardware & software SPI
#define LIS3DH_CS 5
#define CLICKTHRESHHOLD 5

const int CrackLEDR = 6;
const int CrackLEDG = 7;
const int DataIndicatorPin = 8; //Blue of RGB LED
float ResultantAcceleration = 0;
float NewResultantAcceleration = 0;
const int DropThreshold = 4;
const int CrackThreshold = 8;

File myFile;

// software SPI
Adafruit_LIS3DH lis = Adafruit_LIS3DH(LIS3DH_CS, LIS3DH_MOSI, LIS3DH_MISO, LIS3DH_CLK);
// hardware SPI
//Adafruit_LIS3DH lis = Adafruit_LIS3DH(LIS3DH_CS);
// I2C
//Adafruit_LIS3DH lis = Adafruit_LIS3DH();


void WriteToCard();


void setup(void) {

  //-------------------------------------------------
  //Setting up Indicator lights
  pinMode(CrackLEDR, OUTPUT);
  pinMode(CrackLEDG, OUTPUT);
  pinMode(DataIndicatorPin, OUTPUT);

  digitalWrite(CrackLEDR, LOW);
  digitalWrite(CrackLEDG, HIGH);
  digitalWrite(DataIndicatorPin, LOW);
  //-------------------------------------------------

  Serial.begin(9600);
  while (!Serial) delay(10);     // will pause Zero, Leonardo, etc until serial console opens

  if (! lis.begin(0x18)) {   // change this to 0x19 for alternative i2c address
    Serial.println("Couldnt start");
    while (1) yield(); 
  }


  //-----------------------------------------------------------------------------------
  //Detect SD Card
  Serial.print("Initializing SD card...");
  //SD CD on pin 10
  if (!SD.begin(10)) {
    Serial.println("initialization failed!");
    while (1);
  }
  Serial.println("initialization done.");
  //-----------------------------------------------------------------------------------


  //Detect Accelerometer
  Serial.println("LIS3DH found!");

  // lis.setRange(LIS3DH_RANGE_4_G);   // 2, 4, 8 or 16 G!

  Serial.print("Range = "); Serial.print(2 << lis.getRange());
  Serial.println("G");

  // lis.setDataRate(LIS3DH_DATARATE_50_HZ);
  Serial.print("Data rate set to: ");
  switch (lis.getDataRate()) {
    case LIS3DH_DATARATE_1_HZ: Serial.println("1 Hz"); break;
    case LIS3DH_DATARATE_10_HZ: Serial.println("10 Hz"); break;
    case LIS3DH_DATARATE_25_HZ: Serial.println("25 Hz"); break;
    case LIS3DH_DATARATE_50_HZ: Serial.println("50 Hz"); break;
    case LIS3DH_DATARATE_100_HZ: Serial.println("100 Hz"); break;
    case LIS3DH_DATARATE_200_HZ: Serial.println("200 Hz"); break;
    case LIS3DH_DATARATE_400_HZ: Serial.println("400 Hz"); break;

    case LIS3DH_DATARATE_POWERDOWN: Serial.println("Powered Down"); break;
    case LIS3DH_DATARATE_LOWPOWER_5KHZ: Serial.println("5 Khz Low Power"); break;
    case LIS3DH_DATARATE_LOWPOWER_1K6HZ: Serial.println("16 Khz Low Power"); break;
  }


   lis.setClick(2, CLICKTHRESHHOLD);

}




  void loop() {

    while (true) {
      uint8_t click = lis.getClick();
      if (click == 0) return;
      if (! (click & 0x30)) return;
      Serial.print("Click detected (0x"); Serial.print(click, HEX); Serial.print("): ");
      if (click & 0x10){   
            
      myFile = SD.open("Data.txt", FILE_WRITE);
       digitalWrite(DataIndicatorPin, HIGH);
       
        break;
      }
      myFile.println("New Data Set");
      myFile.println("-------------------------------------");
    }
    while (true) {
      sensors_event_t event;
      lis.getEvent(&event);
      ResultantAcceleration = sqrt(sq(abs(event.acceleration.x)) + sq(abs(event.acceleration.y)) + sq(abs(event.acceleration.z)));
    WriteToCard();
    NewResultantAcceleration = sqrt(sq(abs(event.acceleration.x)) + sq(abs(event.acceleration.y)) + sq(abs(event.acceleration.z)));
    if (abs(ResultantAcceleration - NewResultantAcceleration) > DropThreshold) break;
    if (abs(ResultantAcceleration - NewResultantAcceleration) > CrackThreshold){
      digitalWrite(CrackLEDG, LOW);
      digitalWrite(CrackLEDR, HIGH);
      break;
    }
    }
    for (int i=0;i<25;i++){
        WriteToCard();
      }
    myFile.println("-------------------------------------");
    myFile.close();
    digitalWrite(DataIndicatorPin, LOW);
delay (5000);
  

}

void WriteToCard(){
        sensors_event_t event;
      lis.getEvent(&event);

      ResultantAcceleration = sqrt(sq(abs(event.acceleration.x)) + sq(abs(event.acceleration.y)) + sq(abs(event.acceleration.z)));
      /* Display the results (acceleration is measured in m/s^2) */
      Serial.print("\t\tX: "); Serial.print(event.acceleration.x);
      Serial.print(" \tY: "); Serial.print(event.acceleration.y);
      Serial.print(" \tZ: "); Serial.print(event.acceleration.z);
      Serial.println(" m/s^2 ");
      Serial.println("Total Acceleration"); Serial.print(ResultantAcceleration);
      Serial.println();

      myFile.print(event.acceleration.x); myFile.print(" ");
      myFile.print(event.acceleration.y); myFile.print(" ");
      myFile.print(event.acceleration.z); myFile.print(" ");
      myFile.print(ResultantAcceleration); myFile.print(" ");
      myFile.println(" ");

      delay(200);

      
}

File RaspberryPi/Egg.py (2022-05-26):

from machine import ADC, Pin
import utime

X = 26
Y = 27
Z = 29
cutoff = 40000

Rpin = 0
Gpin = 1

RLED=Pin(Rpin,Pin.OUT)
GLED=Pin(Gpin,Pin.OUT)

GLED.toggle()

Xref = ADC(Pin(X))
Yref = ADC(Pin(Y))
Zref = ADC(Pin(Z))
    


while (True): 
    Xval = Xref.read_u16()
    Yval = Yref.read_u16()
    Zval = Zref.read_u16()

    utime.sleep(0.05)


    Xval2 = Xref.read_u16()
    Yval2 = Yref.read_u16()
    Zval2 = Zref.read_u16()
    
    if (Xval - Xval2 > cutoff or Yval - Yval2 > cutoff or Zval - Zval2 > cutoff):
        GLED.toggle()
        RLED.toggle()
        utime.sleep(3)
        GLED.toggle()
        RLED.toggle()
    print(Xval)

    
          

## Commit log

2022-07-01 Moved Files around, added Arduino folder and SD library to folder.
2022-07-01 added Arduino Main.ino
2022-07-12 Updated Main file with SD card and Accelerometer information. It is set to a 30 second Read/Write timer. Pins for LEDs have been initialized and declared but are not yet implemented.
2022-07-12 Made edits to Main.ino, added in single tap detection, LED commands, and resultant acceleration calculations. Thresholds still need adjusting (Crack and Tap), break from infinite logging loop needs w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
2022-07-13 Edited some code, Created schematic for egg main board
    [Adafruit LIS3DH Original.brd, Adafruit LIS3DH Original.sch, Adafruit LIS3DH.brd, Adafruit LIS3DH.sch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]
2022-07-13 Created Egg Main board, needs different power connector. Needs secondary board
    [ElectronicEggDrop.kicad_pcb, ElectronicEggDrop.kicad_sch]
2022-07-13 added LIS3DH
    [ElectronicEggDrop.kicad_pcb, ElectronicEggDrop.kicad_sch]
2022-07-15 Finished V1 of the Control and Sensor Egg boards, 3D models created by FreeCAD. Need to fix code, assemble boards in FreeCAD, and create 3D printed housing
    [ControlEgg.FCStd, ElectronicEggDrop.kicad_pcb, ElectronicEggDrop.kicad_sch, ElectronicEggDrop.step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]
2022-07-15 added STEP of board
    [ControlEgg-ElectronicEggDrop.step, SensorEgg-SensorEgg.step]
2022-07-15 added STL models
    [ControlEgg-ElectronicEggDrop.stl, SensorEgg-SensorEgg.stl]
2022-07-15 Started Assembly of boards, added Arduino nano and LIS3dh Boards, found new footprints for LIS3DH and SDreader, need to implement them.
    [0805 Chip SMD LED (2x1.2mm).step.SLDPRT, 102 RESISTOR PACK.SLDPRT, 189 RESISTOR PACK.SLDPRT, 1x15 Male Pin Header.SLDPRT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]
2022-07-20 Finished the PCBs
    [Ada microsd.SLDPRT, Ada microsd.STEP, ElectronicEggDrop.kicad_pcb, ElectronicEggDrop.kicad_sch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]
2022-07-20 Added Gerber Files
    [ElectronicEggDrop-B_Cu.gbr, ElectronicEggDrop-B_Mask.gbr, ElectronicEggDrop-B_Paste.gbr, ElectronicEggDrop-B_Silkscreen.gbr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]
2022-07-21 Finished V1 of boards, sent them out for manufacturing, BOM genereated but needs editing.
    [ElectronicEggDrop-B_Cu.gbr, ElectronicEggDrop-B_Mask.gbr, ElectronicEggDrop-B_Paste.gbr, ElectronicEggDrop-B_Silkscreen.gbr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]
2022-08-11 Created an Egg V2, Version one SensorEgg PCB did not work due to flipped footprints. V2 will be a singal board.
    [ControlEgg-ElectronicEggDrop.step, ControlEgg-ElectronicEggDrop.stl, ControlEgg.FCStd, ElectronicEggDrop.kicad_pcb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]
2022-08-19 Updated v2, pretty much ready t order. May experiment with reducing amountof spi wires used.
    [ElectronicEggDrop.kicad_sch]

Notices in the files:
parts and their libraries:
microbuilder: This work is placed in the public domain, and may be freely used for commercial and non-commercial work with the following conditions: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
